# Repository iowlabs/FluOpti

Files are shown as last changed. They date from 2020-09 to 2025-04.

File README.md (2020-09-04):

# FluOpti
Este proyecto consiste en la realización de un control integrado para la iluminación del proyecto FluOpti. Más información respecto al poyecto se puede encontrar en los siguientes enlaces:
1. https://docs.google.com/document/d/1PmyignsIkzQdomBdSQQ2lFlBKneosc83GTr52-iTTBQ/edit?usp=sharing
2. [Git](https://github.com/SynBioUC/FluoPi/tree/master/Hardware_design_files/PCB)
3. [OSF](https://osf.io/dy6p2/)
4. [Manual de diseño de proyectos de LEDs estandar](https://www.overleaf.com/4759732231nspqcngnnhdq)

## Descripción de problema electrónico
El sistema consiste en un dispositivo que permite observar muestras biológicas, a las cuales se les realizan procesos de activación genética por medio de otpogenética. 
En la práctica, el dispositivo consiste en una cámara conectada a una raspberry, la que permite observar las muestras, un set de LEDs, los que permiten realizar los procesos optogenéticos, y la respectiva electrónica de control. 

Los LEDs que se deben controlar realizan 3 tareas distintas:
1. Excitar la muestra para poder adquirir imágenes de fluorescencia: LEDs azules.
2. Iluminar la muestra para obtener imágenes de campo claro que permitan medir el crecimiento de las colonias bacterianas de manera apropiada: LEDs blancos.
3. Generar estímulos para activación de procesos optogenéticos. Estos LEDs son de longitudes de onda específicas dependiendo del gen que se desee activar/desactivar: LEDs rojos y verdes.

El proyecto también considera la necesidad de implementar sensores que permitan calibrar el sistema y monitorear variables determinadas, tales como intensidad o temperatura.

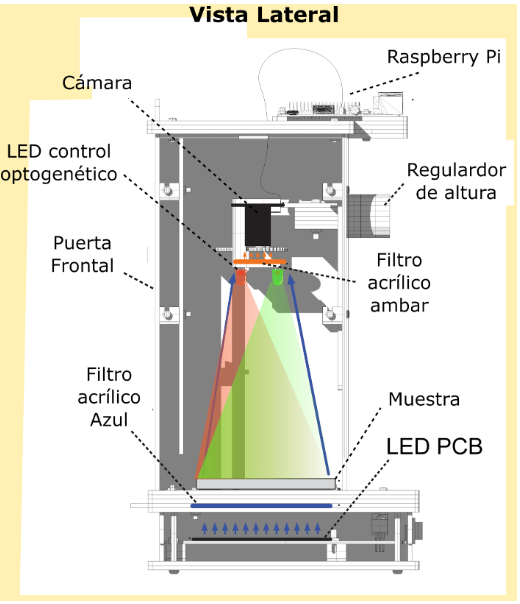
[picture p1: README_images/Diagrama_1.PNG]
Diagrama General


## Requerimientos

### Requerimientos generales
A continuación se enlista un set de requerimientos generales del proyecto:
1. Implementar una electrónica compatible con los componentes actuales disponibles.
2. Proponer una solución completa al problema.
3. Considerar diseños modulares que permitan adaptarse a parámetros futuros.

### Requerimientos específicos

A continuación se enlista un set de requerimientos específicos del proyecto:
1. Los LEDs azules empleados para iluminar la muestra corresponden a los [Super Bright 5mm Blue](https://www.superbrightleds.com/moreinfo/through-hole/5mm-blue-led-120-degree-viewing-angle-flat-tipped-1200-mcd/265/1192/):
   * Longitud de onda: 470nm
   * Forward current: 30mA @ 3.3V
   * Peak forward current: 100mA
   * Max voltage forward: 3.8V
   
2. Actualmente, se está pensando en una placa de LEDs azules con distribución física del tipo circular. Esto implicaría una cantidad de 55 LEDs. En la siguiente imagen se muestra esta topología propuesta:

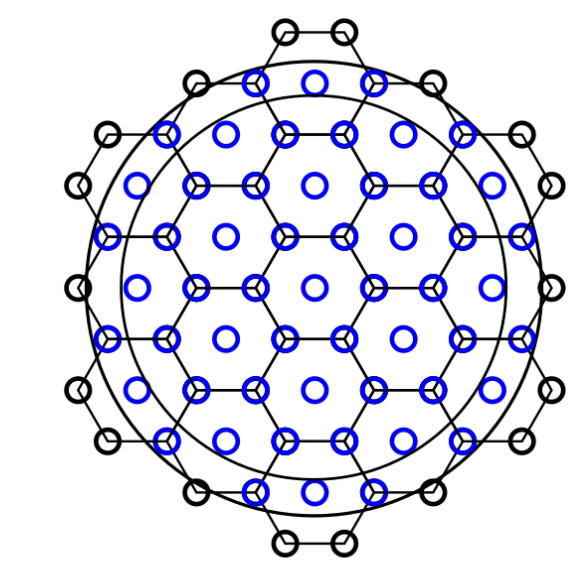
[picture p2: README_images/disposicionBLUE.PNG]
Propuesta nueva disposición LEDs azules


3. Los LEDs verdes empleados para la activación de genes corresponden a los [Kingbright WP7083ZGD/G](http://www.kingbrightusa.com/images/catalog/SPEC/WP7083ZGD-G.pdf):
   * Longitud de onda: 520nm
   * Forward current (typ): 20mA @ 3.2V
   * Peak forward current: 100mA
   * Max voltage forward: 4V
   
4. Los LEDs rojos empleados para la desactivación de genes corresponden a los [Deep-Red 5mm LED](https://www.ledsupply.com/leds/5mm-led-deep-red-660nm-50-degree-viewing-angle):
   * Longitud de onda: 660nm
   * Forward current (typ): 20mA @ 2.2V
   * Peak forward current: 100mA
   * Max voltage forward: 2.8V
   
5. Los LEDs blancos se implementan por medio de una tira LED comercial. Típicamente su operación se caracteriza por:
   * Forward current: 20mA @ 12V
   
6. El control implementado debe corresponder a PWM, con el fin de regular la intensidad lumínica de los LEDs. Se opta por este control debido a su sencilla implementación.

7. El sistema  debe contar con un sistema de distribución de potencia para alimentar todos los sub-módulos, LEDs y raspberry.

8. El sistema debe contar, además, con la posibilidad de leer sensores que permitan medir y calibrar la intensidad de luz proveniente desde los LEDs. Dado que el control se implementa por medio de una raspberry, es necesario utilizar sensores digitales o incluir en el diseño un ADC que permita realizar la conversión. En este último caso será necesaria la inclusión de una etapa que acondicione las señales provenientes desde los sensores.
   
9. El sensor de intensidad lumínica tiene que cumplir:
* Bajo costo
* Fácil de conseguir
* Respuesta plana para los LED Rojo y Verde

Una alternativa es el fototransistor [TEMT6000](https://learn.sparkfun.com/tutorials/temt6000-ambient-light-sensor-hookup-guide/all).

10. El sensor de temperatura es un NTC (termistor). [Aquí](https://www.adafruit.com/product/372) se presenta una alternativa.

11. El heater es del tipo resistivo y se debe poder alimentar con 9V ó 12V. Se debe implementar un control PWM de corriente utilizando un transistor. Una posible alternativa de heater es el [Film Heating Panel](http://www.icstation.com/heating-thin-film-polyimide-heating-plate-panel-25x50mm-b1221-p-9887.html).

### Consideraciones de diseño adicionales
   
1. Consideraciones de operación: El dispositivo debe ser diseñado para funcionar en espacios interiores y dentro de una cápsula cerrada, en la se realiza el análisis de las muestras, por lo que no es necesaria la resistencia al agua o a condiciones de humedad extremas. La placa estará, además, dentro de una caja, por lo que tampoco estará expuesta a polvo u otros contaminantes. Una vez instalado el dispositivo, este permanecerá siempre en el mismo lugar (a menos que se deba extraer por alguna situación en particular), por lo que no es necesario que el diseño considere la exposición a posibles golpes o vibraciones muy significativas.

2. La única etapa del circuito que puede significar un peligro para el usuario es la alimentación, puesto que esta proviene desde la red eléctrica, por lo cual es prudente que la carcasa del producto cumpla con normas acorde al voltaje y corriente de operación, por ejemplo, IP67. Sin embargo, esta protección será ajena al circuito mismo. Es pertinente, de todas formas, la inclusión de disipadores en algunos integrados, en el caso que operen con altas corrientes. Esto, para evitar fallas durante la operación o incluso que se quemen componentes.

## Propuesta
Teniendo presente los requerimientos planteados en la sección anterior se propone una solución basada en el siguiente esquema

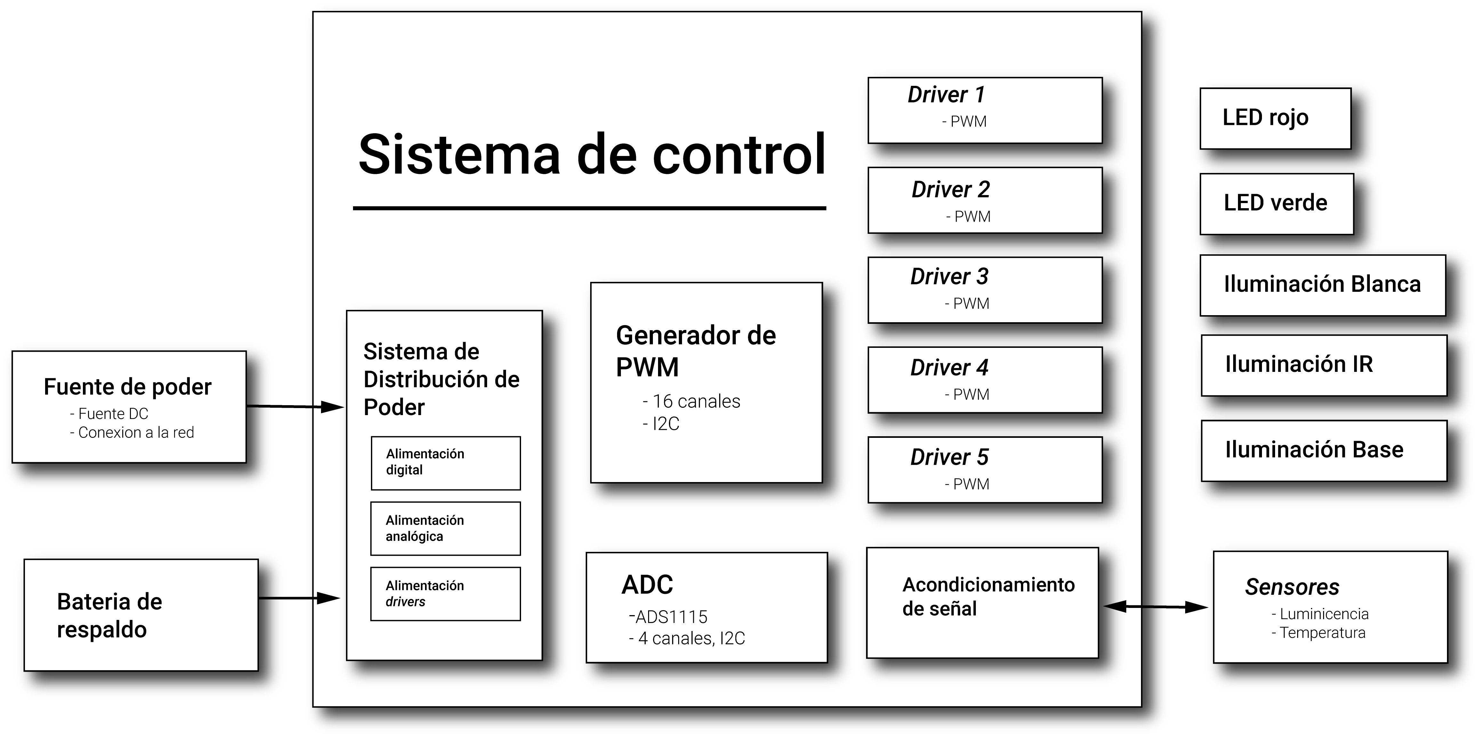
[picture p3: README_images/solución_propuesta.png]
Esquema de la solución electrónica propuesta


El principal criterio de diseño considerado es la modularidad, con el objetivo de poder entregar una solución adaptable y escalable. Los parámetros prácticos de elección de componentes dependen de los requerimientos específicos del sistema. El esquema general consiste en un módulo que genera señales PWM, el cual es controlado por protocolo serial I2C. Este módulo genera 16 señales de PWM permitiendo controlar hasta 16 canales. Estas señales PWM controlan los módulos driver. Estos últimos ajustan la señal PWM a los requerimientos que necesitan los distintos tipos de circuitos de LEDs. Cada driver puede poseer uno o más canales dependiendo de la cantidad de subcircuitos independientes que se deseen controlar por tipo de LED. Del mismo modo, algunas de estas señales de control PWM pueden dejarse a disposición del usuario en caso que necesite controlar una placa con driver ya existente, como es el caso de este proyecto. 

El otro bloque importante es el sistema de distribución de poder, el cual se encarga de generar todos los voltajes necesarios para los distintos bloques y etapas del circuito, dependiendo de cada requerimiento. La idea principal es que la placa reciba una única alimentación y que, internamente, genere los distintos voltajes y corrientes, contribuyendo, así, a la adaptabilidad de la solución.

Por último, la placa considera la inclusión de un ADC de 4 canales, controlado por I2C, el cual permite leer hasta 4 sensores analógicos. Es necesario contar con un ADC, ya que la Raspberry Pi no cuenta con ADC. Esto permite otorgar una alta adaptabilidad, ya que es posible conectar distintos tipos de sensores analógicos, dependiendo de la aplicación. Para esto, la placa considera etapas de acondicionamiento de señal, las cuales se deben configurar para el sensor específico.

### Resumen de características de la solución propuesta

Las principales características de la solución propuesta son:

1. Adaptabilidad: La placa total solo se controla por medio de un bus I2C (3 pines), independiente de la cantidad de LEDs y sensores que se deseen utilizar. 

2. Integración: La disposición de canales de control PWM permite integrar tanto las soluciones existentes como soluciones creadas por distintos fabricantes.

3. Escalabilidad: Gracias a la utilización del protocolo I2C, es posible controlar múltiples de estas placas con una sola Raspberry Pi (o un solo microcontrolador/procesador en general). Si se integran dos placas en serie se puede llegar a disponer de 32 canales de control de LEDs y 8 canales de sensores analógicos. 

A continuación, se describen en detalle los módulos a implementar. Es importante mencionar que se utilizó como guía el [documento tutorial](https://www.overleaf.com/4759732231nspqcngnnhdq) generado en el marco de este proyecto.

### Detalle de módulos

#### ADC
El ADC escogido es el [ADC](https://cdn-shop.adafruit.com/datasheets/ads1115.pdf) de la empresa Texas Instruments. La empresa [adafruit](https://www.adafruit.com/product/1085) posee un módulo autocontenido para integrar este ADC a la Raspberry Pi, así como una completa documentación y las bibliotecas para utilizarlo. 

Las principales características de este ADC se enlistan a continuación

* 4 canales, single-ended.
* 16 bits de resolución
* Voltaje de alimentación entre 2V a 5V
* Interfaz I2C
* Referencia interna

#### Acondicionamiento de señal
Los sensores que se utilizarán permiten implementar el proceso de medición gracias a la variación de sus propiedades eléctricas. En general, estas variaciones se evidencian mediante un cambio de voltaje. En consecuencia, este es el voltaje que debe ser adquirido por el circuito electrónico. Por ello, en primera instancia, se dispone de un circuito divisor que, al ser conectado con el respectivo sensor, permite obtener el voltaje asociado a la medición. En la siguiente figura se muestra un ejemplo de esta conexión circuital, para el caso de un sensor de temperatura del tipo termistor (NTC):

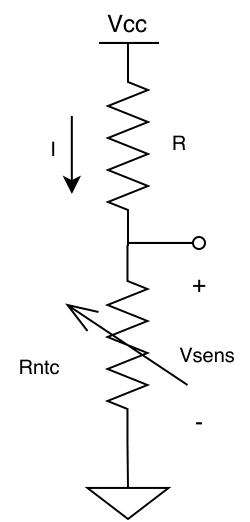
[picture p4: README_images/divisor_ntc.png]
Divisor


Para realizar correctamente la adquisición de las señales desde los sensores es necesario contar con una etapa de acondicionamiento de señal. De esta forma, se asegura que los valores de voltaje que entreguen los sensores se encuentren dentro de los límites que permiten las entradas del ADC y de la Raspberry. No solo es deseable que se opere dentro de los límites, sino también aprovechar el rango de lectura al máximo, es decir, que el voltaje mínimo de medición sea igual (o lo más cercano posible) al voltaje mínimo que permiten los pines del ADC. Y, la misma relación con el voltaje máximo de medición. 

Dado que aún no existe 100% de certeza sobre los sensores a utilizar, se implementó una circuito genérico de acondicionamiento, el cual se compone de una etapa de amplificación y otra de adición de offset. En la siguiente figura se muestra este circuito:

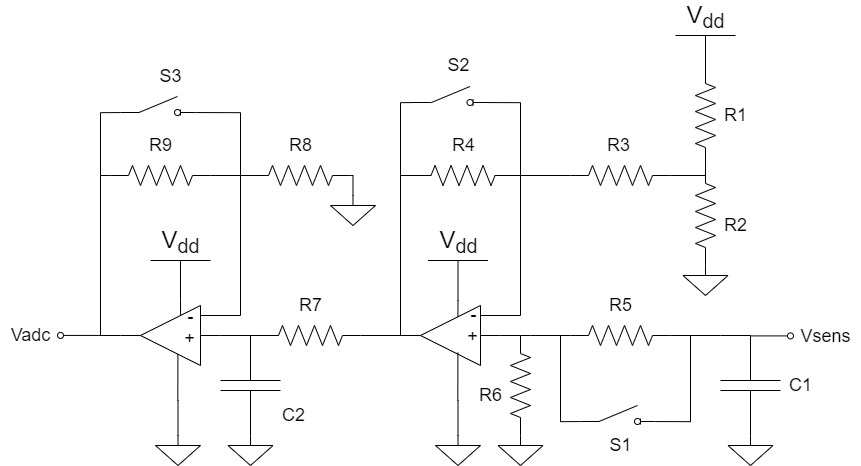
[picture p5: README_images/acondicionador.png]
Acondicionador


Los símbolos de switches corresponden, en la práctica, a un solder jumper, el cual conecta la entrada con la salida solo si se unen con soldadura sus terminales. Si se conectan S1, S2 y S3 el circuito queda configurado como un buffer, lo cual, de todas formas, beneficia a la señal adquirida puesto que el buffer disminuye su impedancia. Conectando o no S1, S2 y S3 se pueden obtener distintas configuraciones: solo amplificador, solo adición de offset, o ambas. Además, los valores de las resistencias se pueden ajustar dependiendo de los sensores que se utilicen, de tal forma de fijar correctamente la ganancia y el offset, según sea el caso.

#### Generador de PWM
La generación de PWM se realiza por medio de un circuito integrado [PCA9685](https://cdn-shop.adafruit.com/datasheets/PCA9685.pdf). La empresa [adafruit](https://www.adafruit.com/product/2928) posee un módulo autocontenido para integrar este módulo a la Raspberry Pi, así como una documentación completa y las bibliotecas para utilizarlo. 

Principales características:

* 16 canales dimeables por PWM.
* 12 bits de resolución
* Voltaje de alimentación etre 2.3V a 5.5V
* Interfaz I2C

#### Driver de baja corriente

Para los canales de bajo consumo de corriente, tales como los arreglos de LEDs rojos y verdes, se utilizará el integrado [ULN2803](https://www.electroschematics.com/wp-content/uploads/2013/07/uln2803a-datasheet.pdf). Este integrado implementa un arreglo de 8 transistores tipo darlington, haciendo posible el control de hasta 8 canales en un único integrado.

Principales características:

* Arreglo de 8 canales
* Poseen alimentación común
* La corriente máxima por canal es de 500mA, pudiendo aumentar esta cantidad si se consideran canales en paralelo.

#### Driver de alta corriente
Para los canales de alto consumo se utilizará un transistor mosfet [IRF740](https://datasheet.lcsc.com/szlcsc/1808281645_Infineon-Technologies-IRF7402TRPBF_C169089.pdf). Es necesario contar con un transistor por canal. Y, para casos de alta corriente (superiores a 1A) es necesario considerar la inclusión de disipadores (heatsink) o pads de disipación que permitan una evacuación efectiva del calor.

Principales características:

* Altas frecuencias de switching
* Bajo consumo de operación 
* Control de hasta 10A (ó 40A en corrientes pulsantes)
* Simple implementación

#### Sistema de distribución de poder

Como se mencionará más adelante, la alimentación que llegará al circuito electrónico implementado será de 12VDC, por lo que es necesario contar con convertidores de voltaje DC-DC para generar los distintos voltajes de alimentación que se requieren en el circuito. En particular, es necesario generar 5V y 3.3V para alimentar los circuitos analógicos y digitales, y un set de voltajes para alimentar los distintos arreglos de LEDs y el Heater. Se decidió disponer de los siguientes voltajes para este último uso: 9V, 16V, 20V y 24V. A continuación se especifican los convertidores empleados para generar cada uno de los voltajes mencionados.

##### 5V
* Integrado: [LM2596R-5.0](https://datasheet.lcsc.com/szlcsc/1811131510_HTC-Korea-TAEJIN-Tech-LM2596R-5-0_C77782.pdf)
* Tipo: Step-down, regulador switching
* Frecuencia de switcheo: 150kHz
* Corriente máxima de salida: 3A

##### 3.3V
* Integrado: [AP2112K-3.3](https://datasheet.lcsc.com/szlcsc/1809192242_Diodes-Incorporated-AP2112K-3-3TRG1_C51118.pdf)
* Tipo: LDO, regulador lineal
* Corriente máxima de salida: 600mA

##### 9V
* Integrado: [LM2696SX-ADJ](https://datasheet.lcsc.com/szlcsc/1809192335_Texas-Instruments-LM2596SX-ADJ-NOPB_C29781.pdf)
* Tipo: Step-down, regulador switching ajustable (voltaje de salida es configurable según indicaciones de conexión en el datasheet)
* Frecuencia de switcheo: 150kHz
* Corriente máxima de salida: 3A

##### 16V, 20V, 24V
* Integrado: [XL6008E1](https://datasheet.lcsc.com/szlcsc/1809200019_XLSEMI-XL6008E1_C73012.pdf)
* Tipo: Step-up, regulador switching ajustable (voltaje de salida es configurable según indicaciones de conexión en el datasheet)
* Frecuencia de switcheo: 400kHz
* Corriente máxima de salida: 3A

#### Fuente de alimentación

Dado que el circuito electrónico funcionará con alimentación DC es necesario emplear una fuente DC que se enchufe directamente a la red y que entegue un voltaje de salida continuo. En particular, se decidió emplear una [fuente DC conmutada](https://afel.cl/producto/fuente-de-poder-12v-10a-120w/). Sus principales características son:

* Voltaje de entrada: 100-120VAC / 60Hz, **200-240VAC / 50Hz**
* Voltaje de salida: 12V
* Corriente máxima de salida: 10A
* Potencia máxima de salida: 120W

## Esquemático

En la siguiente figura se muestra el diagrama de bloques del esquemático implementado

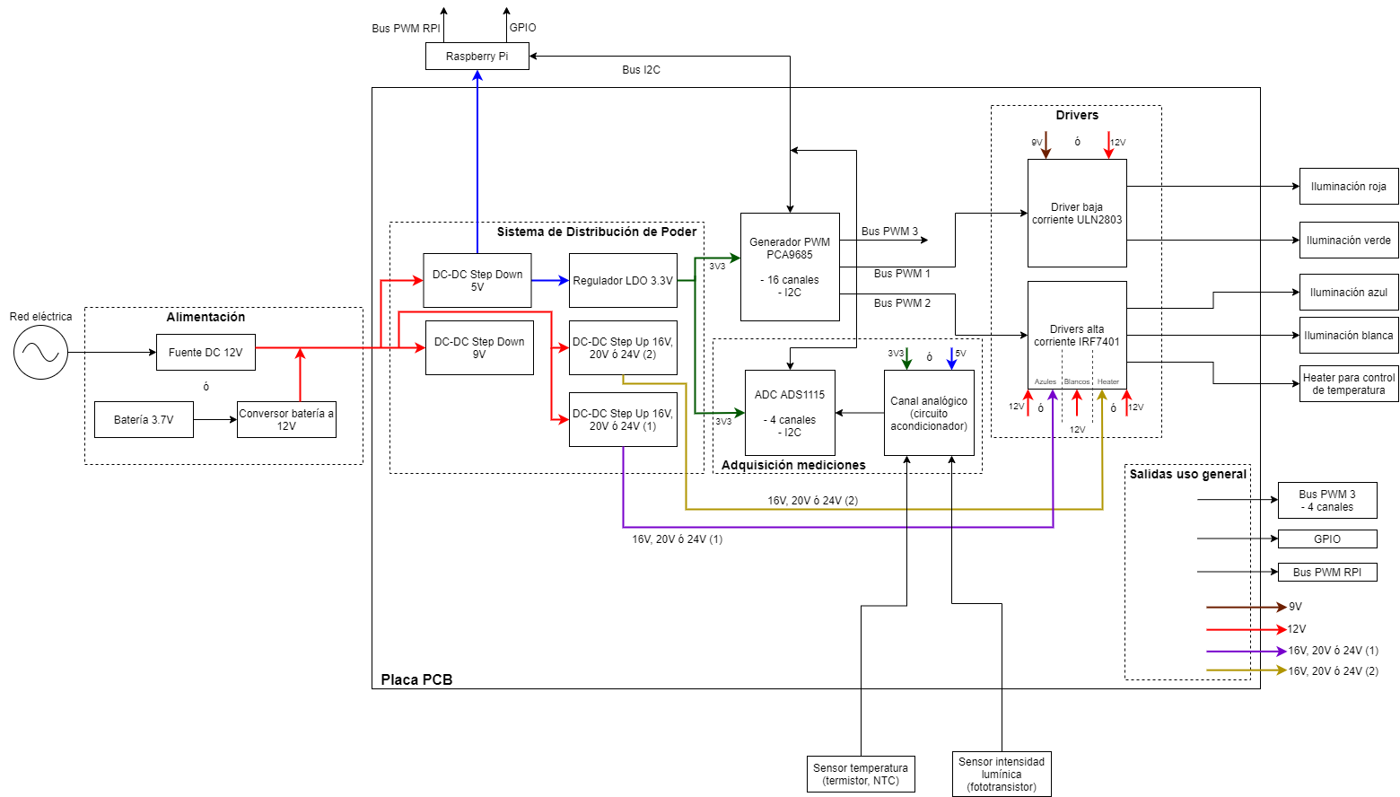
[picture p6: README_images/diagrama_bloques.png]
Diagrama de bloques del esquemático


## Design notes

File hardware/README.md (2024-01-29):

# FluOpti Electrónica

FluOpti es una dispositivo controlador de LEDs para aplicaciones optogenéticas dentro del contexto del proyecto FluOpti.

La placa desarrollada contiene la electrónica necesaria para controlar fuentes de iluminación de alto consumo basadas en LEDS. Dependiendo de la cantidad de LEDs utilizadas y el tipo de conexión en que se dispongan estas matrices de LEDs pueden variar tanto en consumo como el el voltaje de operación.

Es por esto que la electrónica diseñada fue desarrollada considerando flexibilidad en su implementación para abordar un gran  numero de escenarios.

Cuenta con 4 canales de alta potencia para aborar cargas de 24 20 16 12 V configurables y potencias de ahasta

### Features

 La placa cuenta principalmente con 4 canales para controlar canales de LEDS

 - Canal de alta potencia para LEDs azules
 - 3 canales de baja potencia para LEDs Rojos, Verdes, Blancas.

Adicionalmente la placa implementa un controlador de temperatura, para esto cuenta con la electrónica necesaria para drivear 2 heaters resistivos, y con la capacidad de conectar hasta 4 sensores de temperatura NTC analógicos.

## Descripción de Hardware

El esquema presentado en la siguiente figura presenta una descripción general de la estructura del hardware desarrollado.  

Esquema de la solución electrónica propuesta

El principal criterio de diseño considerado es la modularidad, con el objetivo de poder entregar una solución adaptable y escalable. El esquema general consiste en un módulo que genera señales PWM, el cual es controlado por protocolo serial I2C. Este módulo genera 16 señales de PWM permitiendo controlar hasta 16 canales. Estas señales PWM controlan los módulos driver que se encargan de adaptarse a los requerimientos de corriente y voltaje de las cargas asociadas. Cada driver puede poseer uno o más canales dependiendo de la cantidad de subcircuitos independientes que se deseen controlar por tipo de LED. Del mismo modo, algunas de estas señales de control PWM fueron dejadas a disposición del usuario en caso que necesite controlar una placa con driver ya existente, como es el caso de este proyecto (compatibilidad con diseños anteriores).

El otro bloque importante es el sistema de distribución de poder, el cual se encarga de generar todos los voltajes necesarios para los distintos bloques y etapas del circuito, dependiendo de cada requerimiento. La idea principal es que la placa reciba una única alimentación y que, internamente, genere los distintos voltajes y corrientes, contribuyendo, así, a la adaptabilidad de la solución.

Por último, la placa considera la inclusión de un ADC de 4 canales, controlado por I2C, el cual permite leer hasta 4 sensores analógicos para implementar los sensores de corriente. Es necesario contar con un ADC, ya que la Raspberry Pi no cuenta con ADC. Esto permite otorgar una alta adaptabilidad, ya que es posible conectar distintos tipos de sensores analógicos, dependiendo de la aplicación. Para esto, la placa considera etapas de acondicionamiento de señal, las cuales se deben configurar para el sensor específico.

### Resumen de características de la solución propuesta

Las principales características de la solución propuesta son:

1. Adaptabilidad: La placa total solo se controla por medio de un bus I2C (3 pines), independiente de la cantidad de LEDs y sensores que se deseen utilizar.

2. Integración: La disposición de canales de control PWM permite integrar tanto las soluciones existentes como soluciones creadas por distintos fabricantes.

3. Escalabilidad: Gracias a la utilización del protocolo I2C, es posible controlar múltiples de estas placas con una sola Raspberry Pi (o un solo microcontrolador/procesador en general). Si se integran dos placas en serie se puede llegar a disponer de 32 canales de control de LEDs y 8 canales de sensores analógicos.

A continuación, se describen en detalle los módulos a implementar. Es importante mencionar que se utilizó como guía el [documento tutorial](https://www.overleaf.com/4759732231nspqcngnnhdq) generado en el marco de este proyecto.

### Detalle de módulos

#### ADC
El ADC escogido es el [ADC](https://cdn-shop.adafruit.com/datasheets/ads1115.pdf) de la empresa Texas Instruments. La empresa [adafruit](https://www.adafruit.com/product/1085) posee un módulo autocontenido para integrar este ADC a la Raspberry Pi, así como una completa documentación y las bibliotecas para utilizarlo.

Las principales características de este ADC se enlistan a continuación

* 4 canales, single-ended.
* 16 bits de resolución
* Voltaje de alimentación entre 2V a 5V
* Interfaz I2C
* Referencia interna

#### Acondicionamiento de señal
Los sensores que se utilizarán permiten implementar el proceso de medición gracias a la variación de sus propiedades eléctricas. En general, estas variaciones se evidencian mediante un cambio de voltaje. En consecuencia, este es el voltaje que debe ser adquirido por el circuito electrónico. Por ello, en primera instancia, se dispone de un circuito divisor que, al ser conectado con el respectivo sensor, permite obtener el voltaje asociado a la medición. En la siguiente figura se muestra un ejemplo de esta conexión circuital, para el caso de un sensor de temperatura del tipo termistor (NTC):

Divisor

Para realizar correctamente la adquisición de las señales desde los sensores es necesario contar con una etapa de acondicionamiento de señal. De esta forma, se asegura que los valores de voltaje que entreguen los sensores se encuentren dentro de los límites que permiten las entradas del ADC y de la Raspberry. No solo es deseable que se opere dentro de los límites, sino también aprovechar el rango de lectura al máximo, es decir, que el voltaje mínimo de medición sea igual (o lo más cercano posible) al voltaje mínimo que permiten los pines del ADC. Y, la misma relación con el voltaje máximo de medición.

Dado que aún no existe 100% de certeza sobre los sensores a utilizar, se implementó una circuito genérico de acondicionamiento, el cual se compone de una etapa de amplificación y otra de adición de offset. En la siguiente figura se muestra este circuito:

Acondicionador

Los símbolos de switches corresponden, en la práctica, a un solder jumper, el cual conecta la entrada con la salida solo si se unen con soldadura sus terminales. Si se conectan S1, S2 y S3 el circuito queda configurado como un buffer, lo cual, de todas formas, beneficia a la señal adquirida puesto que el buffer disminuye su impedancia. Conectando o no S1, S2 y S3 se pueden obtener distintas configuraciones: solo amplificador, solo adición de offset, o ambas. Además, los valores de las resistencias se pueden ajustar dependiendo de los sensores que se utilicen, de tal forma de fijar correctamente la ganancia y el offset, según sea el caso.

#### Generador de PWM
La generación de PWM se realiza por medio de un circuito integrado [PCA9685](https://cdn-shop.adafruit.com/datasheets/PCA9685.pdf). La empresa [adafruit](https://www.adafruit.com/product/2928) posee un módulo autocontenido para integrar este módulo a la Raspberry Pi, así como una documentación completa y las bibliotecas para utilizarlo.

Principales características:

* 16 canales dimeables por PWM.
* 12 bits de resolución
* Voltaje de alimentación etre 2.3V a 5.5V
* Interfaz I2C

#### Driver de baja corriente

Para los canales de bajo consumo de corriente, tales como los arreglos de LEDs rojos y verdes, se utilizará el integrado [ULN2803](https://www.electroschematics.com/wp-content/uploads/2013/07/uln2803a-datasheet.pdf). Este integrado implementa un arreglo de 8 transistores tipo darlington, haciendo posible el control de hasta 8 canales en un único integrado.

Principales características:

* Arreglo de 8 canales
* Poseen alimentación común
* La corriente máxima por canal es de 500mA, pudiendo aumentar esta cantidad si se consideran canales en paralelo.

#### Driver de alta corriente
Para los canales de alto consumo se utilizará un transistor mosfet [IRF740](https://datasheet.lcsc.com/szlcsc/1808281645_Infineon-Technologies-IRF7402TRPBF_C169089.pdf). Es necesario contar con un transistor por canal. Y, para casos de alta corriente (superiores a 1A) es necesario considerar la inclusión de disipadores (heatsink) o pads de disipación que permitan una evacuación efectiva del calor.

Principales características:

* Altas frecuencias de switching
* Bajo consumo de operación
* Control de hasta 10A (ó 40A en corrientes pulsantes)
* Simple implementación

#### Sistema de distribución de poder

Como se mencionará más adelante, la alimentación que llegará al circuito electrónico implementado será de 12VDC, por lo que es necesario contar con convertidores de voltaje DC-DC para generar los distintos voltajes de alimentación que se requieren en el circuito. En particular, es necesario generar 5V y 3.3V para alimentar los circuitos analógicos y digitales, y un set de voltajes para alimentar los distintos arreglos de LEDs y el Heater. Se decidió disponer de los siguientes voltajes para este último uso: 9V, 16V, 20V y 24V. A continuación se especifican los convertidores empleados para generar cada uno de los voltajes mencionados.

##### 5V
* Integrado: [LM2596R-5.0](https://datasheet.lcsc.com/szlcsc/1811131510_HTC-Korea-TAEJIN-Tech-LM2596R-5-0_C77782.pdf)
* Tipo: Step-down, regulador switching
* Frecuencia de switcheo: 150kHz
* Corriente máxima de salida: 3A

##### 3.3V
* Integrado: [AP2112K-3.3](https://datasheet.lcsc.com/szlcsc/1809192242_Diodes-Incorporated-AP2112K-3-3TRG1_C51118.pdf)
* Tipo: LDO, regulador lineal
* Corriente máxima de salida: 600mA

##### 9V
* Integrado: [LM2696SX-ADJ](https://datasheet.lcsc.com/szlcsc/1809192335_Texas-Instruments-LM2596SX-ADJ-NOPB_C29781.pdf)
* Tipo: Step-down, regulador switching ajustable (voltaje de salida es configurable según indicaciones de conexión en el datasheet)
* Frecuencia de switcheo: 150kHz
* Corriente máxima de salida: 3A

##### 16V, 20V, 24V
* Integrado: [XL6008E1](https://datasheet.lcsc.com/szlcsc/1809200019_XLSEMI-XL6008E1_C73012.pdf)
* Tipo: Step-up, regulador switching ajustable (voltaje de salida es configurable según indicaciones de conexión en el datasheet)
* Frecuencia de switcheo: 400kHz
* Corriente máxima de salida: 3A

#### Fuente de alimentación

Dado que el circuito electrónico funcionará con alimentación DC es necesario emplear una fuente DC que se enchufe directamente a la red y que entegue un voltaje de salida continuo. En particular, se decidió emplear una [fuente DC conmutada](https://afel.cl/producto/fuente-de-poder-12v-10a-120w/). Sus principales características son:

* Voltaje de entrada: 100-120VAC / 60Hz, **200-240VAC / 50Hz**
* Voltaje de salida: 12V
* Corriente máxima de salida: 10A
* Potencia máxima de salida: 120W

## Esquemático

En la siguiente figura se muestra el diagrama de bloques del esquemático implementado

Diagrama de bloques del esquemático

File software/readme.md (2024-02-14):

# Hardware

En la Raspberry Pi:
  - pin 3 (GPIO2): SDA
  - pin 5 (GPIO3): SCL
  - pin 6 :        GND

En la tarjeta FLuOpti
  Esquina superior izquierda:<br>
    1 - SCL &emsp; &emsp; &emsp; &emsp; &emsp;8 - PWM in 1<br>
    2 - SDA &emsp; &emsp; &emsp; &emsp; &ensp;&nbsp;7 - PWM in 2<br>
    3 - NotConnected   &emsp; 6 - GPIO1<br>
    4 - GND &emsp; &emsp; &emsp; &emsp; &ensp;5 - GPIO2<br>
  
  Los conectores GPIO y PWM estan diseñados para conectar cualquier pin de la Raspberry Pi, los cuales son clonados a la parte inferior de la placa. *e.g.* puedo conectar el pin15 de la raspberry Pi al conector GPIO1, y luego conectarme directamente al GPIO1 de la parte inferior de la placa para acceder a él.

 De manera alternativa, es preferible usar el conector i2c (esquina superior derecha) para mayor simpleza:<br>
  1 - SCL<br>
  2 - SDA<br>
  3 - GND

<p align="center">
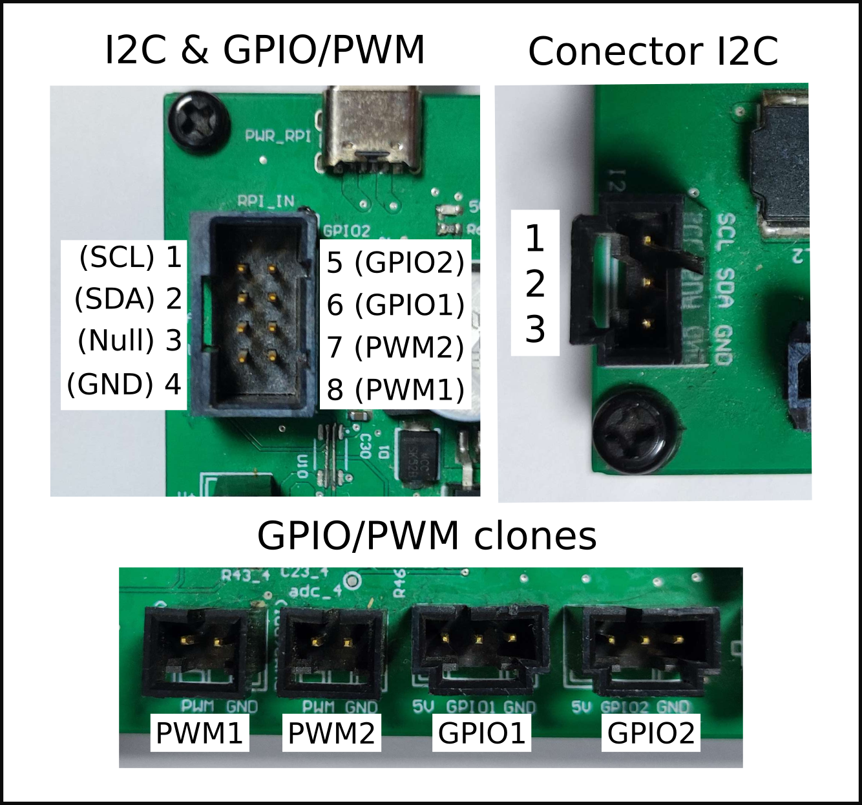
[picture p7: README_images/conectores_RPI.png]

</p>
  
# Instalación

## Sistemas operativos previos a BookWorm

Instalar las librerias necesarias para el funcionamiento de la placa:
```
sudo pip install adafruit-ADS1x15
sudo pip install adafruit-pca9685
sudo pip install simple-pid
```

## Sistema operativo BookWorm
Si se esta usando *BookWorm* como sistema operativo de la Raspberry Pi, es necesario crear un ambiente en el que instalar estas librerias.
Primero asegurarse de tener todo actualizado:
```
sudo apt-get update
sudo apt-get upgrade
sudo apt-get install python3-pip
sudo apt install --upgrade python3-setuptools
sudo apt install python3.11-venv
```

Crear el ambiente *fluop_env*:
```
python3 -m venv fluop_env --system-site-packages
```
y activarlo
```
source fluop_env/bin/activate
```

ahora se deben instalar las librerias en él:
```
pip3 install adafruit-ADS1x15
pip3 install adafruit-pca9685
pip3 install simple-pid
```

Alternativamente se pueden instalar las librerias directamente en el sistema (sin crear ambientes), agregando el comando *--break-system-packages*. Ejemplo:
```
sudo pip install adafruit-ADS1x15 --break-system-packages
```

## Activar comunicación I2C

Ejecutar *sudo raspi-config*, ir a *opciones de interface* y activar la comunicación I2C.

# Solución de problemas

1. Se recomienda instalar el scan de i2c para revisar si los módulos estan:
  - https://learn.adafruit.com/scanning-i2c-addresses/raspberry-pi
  - sudo apt-get install i2c-tools
  - run: i2cdetect -y 1

Se desplegará la lista de direcciones de los módulos conectados:
```
     0  1  2  3  4  5  6  7  8  9  a  b  c  d  e  f
00:                         -- -- -- -- -- -- -- --
10: -- -- -- -- -- -- -- -- -- -- -- -- -- -- -- --
20: -- -- -- -- -- -- -- -- -- -- -- -- -- -- -- --
30: -- -- -- -- -- -- -- -- -- -- -- -- -- -- -- -- 
40: -- -- -- -- -- -- -- -- -- 49 -- -- -- -- -- -- 
50: -- -- -- -- -- -- -- -- -- -- -- -- 5c -- -- -- 
60: -- -- -- -- -- -- -- -- -- -- -- -- -- -- -- -- 
70: 70 -- -- -- -- -- -- --  
```
vemos que hay módulos conectados en 0x49, 0x5c y 0x77

En caso de que los módulos no se encuentren conectados, se desplegará la lista vacia:
```
     0  1  2  3  4  5  6  7  8  9  a  b  c  d  e  f
00:                         -- -- -- -- -- -- -- -- 
10: -- -- -- -- -- -- -- -- -- -- -- -- -- -- -- -- 
20: -- -- -- -- -- -- -- -- -- -- -- -- -- -- -- -- 
30: -- -- -- -- -- -- -- -- -- -- -- -- -- -- -- -- 
40: -- -- -- -- -- -- -- -- -- -- -- -- -- -- -- -- 
50: -- -- -- -- -- -- -- -- -- -- -- -- -- -- -- -- 
60: -- -- -- -- -- -- -- -- -- -- -- -- -- -- -- -- 
70: -- -- -- -- -- -- -- --  
```

# Testeo

En la terminal, navegar hasta el directorio del software */FluOpti/software* (usando comando cd).
(debe estar clonado el repositorio FluOpti en la raspberry).

si se esta utilizando BookWorm como sistema operativo de la raspberry, se debe activar el ambiente en el cual se instalaron los paquetes. Si el ambiente creado se llama *fluop_env*:

```
source fluop_env/bin/activate
```

Luego ejecutamos la rutina de testeo mediante el comando:
```
python3 simple_test.py
```
es necesario chequear que los LEDs esten conectados de manera correspondiente a las posiciones indicadas en el código *FluOpti.py*
```
 self._default_modules  = {
        #MODULE  #CHANNEL    #VALUE
        'R'    :{ 'chan':5, 'value': 0,'status':0},
        'G'    :{ 'chan':6, 'value': 0,'status':0},
        'B'    :{ 'chan':9, 'value': 0,'status':0},
        'W'    :{ 'chan':10, 'value': 0,'status':0},
        'H1'   :{ 'chan':11, 'value': 0,'status':0},
        'H2'   :{ 'chan':12, 'value': 0,'status':0}
        }
```

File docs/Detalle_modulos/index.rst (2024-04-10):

Detalle de módulos
~~~~~~~~~~~~~~~~~~

ADC
^^^

El ADC escogido es el
`ADC <https://cdn-shop.adafruit.com/datasheets/ads1115.pdf>`__ de la
empresa Texas Instruments. La empresa
`adafruit <https://www.adafruit.com/product/1085>`__ posee un módulo
autocontenido para integrar este ADC a la Raspberry Pi, así como una
completa documentación y las bibliotecas para utilizarlo.

Las principales características de este ADC se enlistan a continuación

-  4 canales, single-ended.
-  16 bits de resolución
-  Voltaje de alimentación entre 2V a 5V
-  Interfaz I2C
-  Referencia interna

Acondicionamiento de señal
^^^^^^^^^^^^^^^^^^^^^^^^^^

Los sensores que se utilizarán permiten implementar el proceso de
medición gracias a la variación de sus propiedades eléctricas. En
general, estas variaciones se evidencian mediante un cambio de voltaje.
En consecuencia, este es el voltaje que debe ser adquirido por el
circuito electrónico. Por ello, en primera instancia, se dispone de un
circuito divisor que, al ser conectado con el respectivo sensor, permite
obtener el voltaje asociado a la medición. En la siguiente figura se
muestra un ejemplo de esta conexión circuital, para el caso de un sensor
de temperatura del tipo termistor (NTC):

Divisor

   Divisor

Para realizar correctamente la adquisición de las señales desde los
sensores es necesario contar con una etapa de acondicionamiento de
señal. De esta forma, se asegura que los valores de voltaje que
entreguen los sensores se encuentren dentro de los límites que permiten
las entradas del ADC y de la Raspberry. No solo es deseable que se opere
dentro de los límites, sino también aprovechar el rango de lectura al
máximo, es decir, que el voltaje mínimo de medición sea igual (o lo más
cercano posible) al voltaje mínimo que permiten los pines del ADC. Y, la
misma relación con el voltaje máximo de medición.

Dado que aún no existe 100% de certeza sobre los sensores a utilizar, se
implementó una circuito genérico de acondicionamiento, el cual se
compone de una etapa de amplificación y otra de adición de offset. En la
siguiente figura se muestra este circuito:

Acondicionador

   Acondicionador

Los símbolos de switches corresponden, en la práctica, a un solder
jumper, el cual conecta la entrada con la salida solo si se unen con
soldadura sus terminales. Si se conectan S1, S2 y S3 el circuito queda
configurado como un buffer, lo cual, de todas formas, beneficia a la
señal adquirida puesto que el buffer disminuye su impedancia. Conectando
o no S1, S2 y S3 se pueden obtener distintas configuraciones: solo
amplificador, solo adición de offset, o ambas. Además, los valores de
las resistencias se pueden ajustar dependiendo de los sensores que se
utilicen, de tal forma de fijar correctamente la ganancia y el offset,
según sea el caso.

Generador de PWM
^^^^^^^^^^^^^^^^

La generación de PWM se realiza por medio de un circuito integrado
`PCA9685 <https://cdn-shop.adafruit.com/datasheets/PCA9685.pdf>`__. La
empresa `adafruit <https://www.adafruit.com/product/2928>`__ posee un
módulo autocontenido para integrar este módulo a la Raspberry Pi, así
como una documentación completa y las bibliotecas para utilizarlo.

Principales características:

-  16 canales dimeables por PWM.
-  12 bits de resolución
-  Voltaje de alimentación etre 2.3V a 5.5V
-  Interfaz I2C

Driver de baja corriente
^^^^^^^^^^^^^^^^^^^^^^^^

Para los canales de bajo consumo de corriente, tales como los arreglos
de LEDs rojos y verdes, se utilizará el integrado
`ULN2803 <https://www.electroschematics.com/wp-content/uploads/2013/07/uln2803a-datasheet.pdf>`__.
Este integrado implementa un arreglo de 8 transistores tipo darlington,
haciendo posible el control de hasta 8 canales en un único integrado.

Principales características:

-  Arreglo de 8 canales
-  Poseen alimentación común
-  La corriente máxima por canal es de 500mA, pudiendo aumentar esta
   cantidad si se consideran canales en paralelo.

Driver de alta corriente
^^^^^^^^^^^^^^^^^^^^^^^^

Para los canales de alto consumo se utilizará un transistor mosfet
`IRF740 <https://datasheet.lcsc.com/szlcsc/1808281645_Infineon-Technologies-IRF7402TRPBF_C169089.pdf>`__.
Es necesario contar con un transistor por canal. Y, para casos de alta
corriente (superiores a 1A) es necesario considerar la inclusión de
disipadores (heatsink) o pads de disipación que permitan una evacuación
efectiva del calor.

Principales características:

-  Altas frecuencias de switching
-  Bajo consumo de operación
-  Control de hasta 10A (ó 40A en corrientes pulsantes)
-  Simple implementación

Sistema de distribución de poder
^^^^^^^^^^^^^^^^^^^^^^^^^^^^^^^^

Como se mencionará más adelante, la alimentación que llegará al circuito
electrónico implementado será de 12VDC, por lo que es necesario contar
con convertidores de voltaje DC-DC para generar los distintos voltajes
de alimentación que se requieren en el circuito. En particular, es
necesario generar 5V y 3.3V para alimentar los circuitos analógicos y
digitales, y un set de voltajes para alimentar los distintos arreglos de
LEDs y el Heater. Se decidió disponer de los siguientes voltajes para
este último uso: 9V, 16V, 20V y 24V. A continuación se especifican los
convertidores empleados para generar cada uno de los voltajes
mencionados.

5V
''

-  Integrado:
   `LM2596R-5.0 <https://datasheet.lcsc.com/szlcsc/1811131510_HTC-Korea-TAEJIN-Tech-LM2596R-5-0_C77782.pdf>`__
-  Tipo: Step-down, regulador switching
-  Frecuencia de switcheo: 150kHz
-  Corriente máxima de salida: 3A

.. _v-1:

3.3V
''''

-  Integrado:
   `AP2112K-3.3 <https://datasheet.lcsc.com/szlcsc/1809192242_Diodes-Incorporated-AP2112K-3-3TRG1_C51118.pdf>`__
-  Tipo: LDO, regulador lineal
-  Corriente máxima de salida: 600mA

.. _v-2:

9V
''

-  Integrado:
   `LM2696SX-ADJ <https://datasheet.lcsc.com/szlcsc/1809192335_Texas-Instruments-LM2596SX-ADJ-NOPB_C29781.pdf>`__
-  Tipo: Step-down, regulador switching ajustable (voltaje de salida es
   configurable según indicaciones de conexión en el datasheet)
-  Frecuencia de switcheo: 150kHz
-  Corriente máxima de salida: 3A

16V, 20V, 24V
'''''''''''''

-  Integrado:
   `XL6008E1 <https://datasheet.lcsc.com/szlcsc/1809200019_XLSEMI-XL6008E1_C73012.pdf>`__
-  Tipo: Step-up, regulador switching ajustable (voltaje de salida es
   configurable según indicaciones de conexión en el datasheet)
-  Frecuencia de switcheo: 400kHz
-  Corriente máxima de salida: 3A

Fuente de alimentación
^^^^^^^^^^^^^^^^^^^^^^

Dado que el circuito electrónico funcionará con alimentación DC es
necesario emplear una fuente DC que se enchufe directamente a la red y
que entegue un voltaje de salida continuo. En particular, se decidió
emplear una `fuente DC
conmutada <https://afel.cl/producto/fuente-de-poder-12v-10a-120w/>`__.
Sus principales características son:

-  Voltaje de entrada: 100-120VAC / 60Hz, **200-240VAC / 50Hz**
-  Voltaje de salida: 12V
-  Corriente máxima de salida: 10A
-  Potencia máxima de salida: 120W

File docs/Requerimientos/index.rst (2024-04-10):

Requerimientos
--------------

Requerimientos generales
~~~~~~~~~~~~~~~~~~~~~~~~

A continuación se enlista un set de requerimientos generales del
proyecto: 1. Implementar una electrónica compatible con los componentes
actuales disponibles. 2. Proponer una solución completa al problema. 3.
Considerar diseños modulares que permitan adaptarse a parámetros
futuros.

Requerimientos específicos
~~~~~~~~~~~~~~~~~~~~~~~~~~

A continuación se enlista un set de requerimientos específicos del
proyecto: 1. Los LEDs azules empleados para iluminar la muestra
corresponden a los `Super Bright 5mm
Blue <https://www.superbrightleds.com/moreinfo/through-hole/5mm-blue-led-120-degree-viewing-angle-flat-tipped-1200-mcd/265/1192/>`__:
\* Longitud de onda: 470nm \* Forward current: 30mA @ 3.3V \* Peak
forward current: 100mA \* Max voltage forward: 3.8V

2. Actualmente, se está pensando en una placa de LEDs azules con
   distribución física del tipo circular. Esto implicaría una cantidad
   de 55 LEDs. En la siguiente imagen se muestra esta topología
   propuesta:

Propuesta nueva disposición LEDs azules

   Propuesta nueva disposición LEDs azules

3. Los LEDs verdes empleados para la activación de genes corresponden a
   los `Kingbright
   WP7083ZGD/G <http://www.kingbrightusa.com/images/catalog/SPEC/WP7083ZGD-G.pdf>`__:

   -  Longitud de onda: 520nm
   -  Forward current (typ): 20mA @ 3.2V
   -  Peak forward current: 100mA
   -  Max voltage forward: 4V

4. Los LEDs rojos empleados para la desactivación de genes corresponden
   a los `Deep-Red 5mm
   LED <https://www.ledsupply.com/leds/5mm-led-deep-red-660nm-50-degree-viewing-angle>`__:

   -  Longitud de onda: 660nm
   -  Forward current (typ): 20mA @ 2.2V
   -  Peak forward current: 100mA
   -  Max voltage forward: 2.8V

5. Los LEDs blancos se implementan por medio de una tira LED comercial.
   Típicamente su operación se caracteriza por:

   -  Forward current: 20mA @ 12V

6. El control implementado debe corresponder a PWM, con el fin de
   regular la intensidad lumínica de los LEDs. Se opta por este control
   debido a su sencilla implementación.

7. El sistema debe contar con un sistema de distribución de potencia
   para alimentar todos los sub-módulos, LEDs y raspberry.

8. El sistema debe contar, además, con la posibilidad de leer sensores
   que permitan medir y calibrar la intensidad de luz proveniente desde
   los LEDs. Dado que el control se implementa por medio de una
   raspberry, es necesario utilizar sensores digitales o incluir en el
   diseño un ADC que permita realizar la conversión. En este último caso
   será necesaria la inclusión de una etapa que acondicione las señales
   provenientes desde los sensores.

9. El sensor de intensidad lumínica tiene que cumplir:

-  Bajo costo
-  Fácil de conseguir
-  Respuesta plana para los LED Rojo y Verde

Una alternativa es el fototransistor
`TEMT6000 <https://learn.sparkfun.com/tutorials/temt6000-ambient-light-sensor-hookup-guide/all>`__.

10. El sensor de temperatura es un NTC (termistor).
    `Aquí <https://www.adafruit.com/product/372>`__ se presenta una
    alternativa.

11. El heater es del tipo resistivo y se debe poder alimentar con 9V ó
    12V. Se debe implementar un control PWM de corriente utilizando un
    transistor. Una posible alternativa de heater es el `Film Heating
    Panel <http://www.icstation.com/heating-thin-film-polyimide-heating-plate-panel-25x50mm-b1221-p-9887.html>`__.

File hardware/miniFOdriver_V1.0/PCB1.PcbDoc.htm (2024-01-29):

Reporting Options

# File in Newer Format

Date | : | 02-09-2021
Time | : | 23:33:18
Filename | : | C:\Users\Wac\Desktop\repo_pega\iowlabs\MiniFluOpti\3 - Hardware\miniFOdriver_V1.0\PCB1.PcbDoc

Version | Warning
Release 20.0 | CAUTION - Support of propagation delay for primitives
Release 20.0 | CAUTION - Support for PCB system parameters, used to contain additional data extracted from components

This file was generated by a later version of the software

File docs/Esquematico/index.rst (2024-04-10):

Esquemático
-----------

En la siguiente figura se muestra el diagrama de bloques del esquemático
implementado

Diagrama de bloques del esquemático

   Diagrama de bloques del esquemático

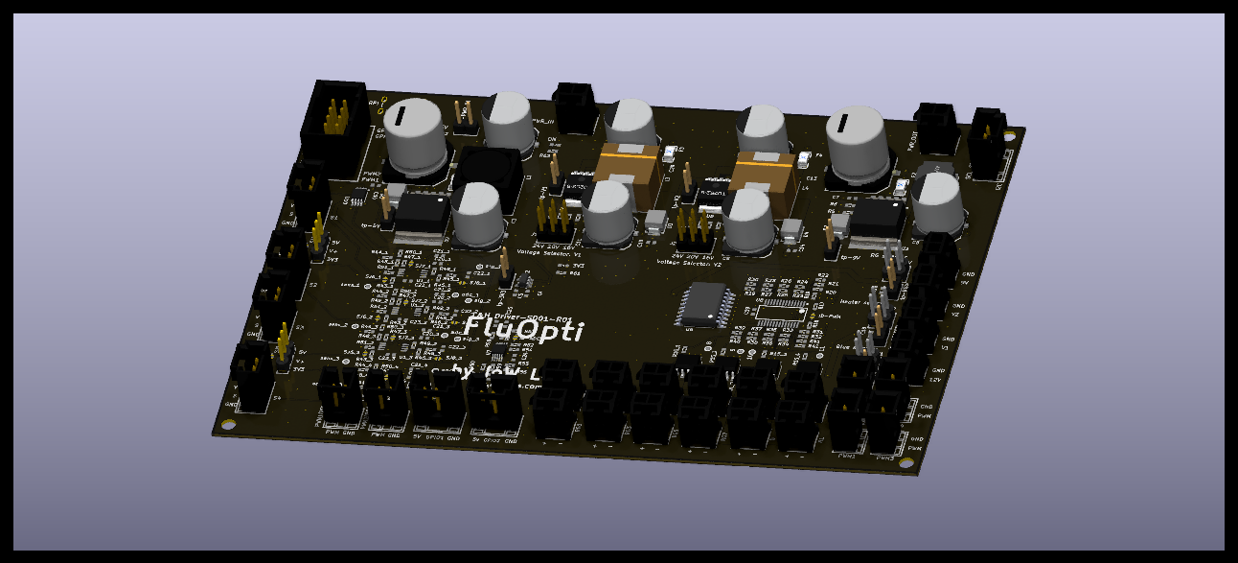
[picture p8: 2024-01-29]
hardware/FOdriver_V2.0/PCBV2.png

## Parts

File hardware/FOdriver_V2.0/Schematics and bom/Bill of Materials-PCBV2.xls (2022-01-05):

Comment | Description | Designator | Footprint | Quantity | Supplier Part Number 1 | Value
TP | Solder test point | 0, 1, 2, 3, 4, 5, 6, 7, 8, 9, 10, 11, 12, 13, 14, 15, adc_1, adc_2, adc_3, adc_4, sens_1, sens_2, sens_3, sens_4, sig_1, sig_2, sig_3, sig_4 | TP | 28
Generic LED | Generic LED SMD | 3V3, 5V, ON | LED0603 | 3 | C125101 (https://octopart-clicks.com/click/altium?manufacturer=Vishay%20Lite-On&mpn=LTST-C191TGKT&seller=LCSC&sku=C125101&country=CL&channel=BOM%20Report)
Power connector 2x1 | Generic Header Power 2pos | 9V, 12V, B, H1, H2, PWR_IN, PWR_OUT, RG1, RG2, RG3, RG4, RG5, RG6, RG7, RG8, V1, V2, W | CONN-TH_430450212 | 18 | C293362 (https://octopart-clicks.com/click/altium?manufacturer=Molex&mpn=43045-0212&seller=LCSC&sku=C293362&country=CL&channel=BOM%20Report)
Pin Header 2x2c | Pin Header 4pos, 2 row, 2.54 pitch | Blue selector, Heater selector, RG selector | HDR-TH_4P-P2.54-V-R2-C2-S2.54_A2541WV-2X2P | 3 | C225517 (https://octopart-clicks.com/click/altium?manufacturer=Loading...&mpn=Loading...&seller=LCSC&sku=C225517&country=CL&channel=BOM%20Report)
Cap pol | Electrolytic Aluminium Capacitor | C1, C12, C15 | CAP_SMD_Electrolytic_10x10 | 3 | C249662 (https://octopart-clicks.com/click/altium?manufacturer=Loading...&mpn=Loading...&seller=LCSC&sku=C249662&country=CL&channel=BOM%20Report) | 47uF
Cap pol | Electrolytic Aluminium Capacitor | C2, C6 | CAP_SMD_Electrolytic_13.5x13.5 | 2 | C178568 (https://octopart-clicks.com/click/altium?manufacturer=Panasonic&mpn=EEE-FK1V681AQ&seller=LCSC&sku=C178568&country=CL&channel=BOM%20Report) | 680uF
Cap pol | Electrolytic Aluminium Capacitor | C3, C8 | CAP_SMD_Electrolytic_10x10 | 2 | C336488 (https://octopart-clicks.com/click/altium?manufacturer=Panasonic&mpn=EEE-1VA331UAP&seller=LCSC&sku=C336488&country=CL&channel=BOM%20Report) | 330uF
Cap Semi | Capacitor (Semiconductor SIM Model) | C4, C5 | 1608[0603] | 2 | C59782 (https://octopart-clicks.com/click/altium?manufacturer=Samsung&mpn=CL10B105KO8NNNC&seller=LCSC&sku=C59782&country=CL&channel=BOM%20Report) | 1uF
Cap Semi | Capacitor (Semiconductor SIM Model) | C7 | 1608[0603] | 1 | C152947 (https://octopart-clicks.com/click/altium?manufacturer=Loading...&mpn=Loading...&seller=LCSC&sku=C152947&country=CL&channel=BOM%20Report) | 1.5nF
Cap pol | Electrolytic Aluminium Capacitor | C9, C11 | CAP_SMD_Electrolytic_10x10 | 2 | C134732 (https://octopart-clicks.com/click/altium?manufacturer=Loading...&mpn=Loading...&seller=LCSC&sku=C134732&country=CL&channel=BOM%20Report) | 220uF
Cap Semi | Capacitor (Semiconductor SIM Model) | C10, C13, C14, C16, C17, C18, C29 | 1608[0603] | 7 | C15849 (https://octopart-clicks.com/click/altium?manufacturer=Samsung&mpn=CL10A105KB8NNNC&seller=LCSC&sku=C15849&country=CL&channel=BOM%20Report) | 1uF
Cap Semi | Capacitor (Semiconductor SIM Model) | C19, C20_1, C20_2, C20_3, C20_4 | 1608[0603] | 5 | C1691 (https://octopart-clicks.com/click/altium?manufacturer=Samsung&mpn=CL10A106MQ8NNNC&seller=LCSC&sku=C1691&country=CL&channel=BOM%20Report) | 10uF
Cap Semi | Capacitor (Semiconductor SIM Model) | C21_1, C21_2, C21_3, C21_4, C22_1, C22_2, C22_3, C22_4, C23_1, C23_2, C23_3, C23_4 | 1608[0603] | 12 | C519410 (https://octopart-clicks.com/click/altium?manufacturer=Loading...&mpn=Loading...&seller=LCSC&sku=C519410&country=CL&channel=BOM%20Report) | 100pF
Cap Semi | Capacitor (Semiconductor SIM Model) | C24, C25, C26, C27, C28, C30 | 1608[0603] | 6 | C386152 (https://octopart-clicks.com/click/altium?manufacturer=Taiyo%20Yuden&mpn=UMK107B104KAHT&seller=LCSC&sku=C386152&country=CL&channel=BOM%20Report) | 100nF
Schottky Diode | Schottky Diodes | D1, D2, D3, D4 | SMB_L4.6-W3.6-LS5.3-RD | 4 | C139945 (https://octopart-clicks.com/click/altium?manufacturer=MCC&mpn=SK32B-LTP&seller=LCSC&sku=C139945&country=CL&channel=BOM%20Report)
Generic Fuse | SMD Fuse | F1, F2, F3, F4 | F1206 | 4 | C310980 (https://octopart-clicks.com/click/altium?manufacturer=Loading...&mpn=Loading...&seller=LCSC&sku=C310980&country=CL&channel=BOM%20Report)
Generic Header 3x1 | Generic Header 3pos, 1 row, 2.54 pitch | GPIO1, GPIO2, I2C, S1, S2, S3, S4 | CONN-TH_A2547WV-3P | 7 | C239378 (https://octopart-clicks.com/click/altium?manufacturer=CJT%20Connectors&mpn=A2547WV-3P&seller=LCSC&sku=C239378&country=CL&channel=BOM%20Report)
sj | solder jumper generic | ID-ADC, ID-PWM, SJ1, SJ2, SJ3, SJ4, SJ6_1, SJ6_2, SJ6_3, SJ6_4, SJ7_1, SJ7_2, SJ7_3, SJ7_4, SJ8_1, SJ8_2, SJ8_3, SJ8_4 | SJ2 | 18
Pin Header 3x2 | Pin Header 6pos, 2 row, 2.54 pitch | J1, J2 | HDR-TH_6P-P2.54-V-R2-C3-S2.54_A2541WV-2X3P | 2 | C225518 (https://octopart-clicks.com/click/altium?manufacturer=Loading...&mpn=Loading...&seller=LCSC&sku=C225518&country=CL&channel=BOM%20Report)
Pin Header 3x1 | Pin Header 3pos, 1 row, 2.54 pitch | L, T | HDR-TH_3P-P2.54-V | 2 | C225478 (https://octopart-clicks.com/click/altium?manufacturer=Loading...&mpn=Loading...&seller=LCSC&sku=C225478&country=CL&channel=BOM%20Report)
Inductor | Inductor SMD | L1 | IND-SMD_L12.5-W12.5_SMDRS1275 | 1 | C238002 (https://octopart-clicks.com/click/altium?manufacturer=Loading...&mpn=Loading...&seller=LCSC&sku=C238002&country=CL&channel=BOM%20Report) | 68uH
Inductor | Inductor SMD | L2 | IND-SMD_L8.0-W8.0 | 1 | C280555 (https://octopart-clicks.com/click/altium?manufacturer=Loading...&mpn=Loading...&seller=LCSC&sku=C280555&country=CL&channel=BOM%20Report) | 15uH
Inductor | Inductor SMD | L3, L4 | IND-SMD_L12.3-W12.3 | 2 | C9400 (https://octopart-clicks.com/click/altium?manufacturer=Loading...&mpn=Loading...&seller=LCSC&sku=C9400&country=CL&channel=BOM%20Report) | 33uH
Generic header 2x1 | Generic Header 2pos, 1 row, 2.54 pitch | PWM1, PWM1(RPI), PWM2, PWM2(RPI), PWM3, PWM4 | CONN-TH_A2547WV-2P | 6 | C239377 (https://octopart-clicks.com/click/altium?manufacturer=Loading...&mpn=Loading...&seller=LCSC&sku=C239377&country=CL&channel=BOM%20Report)
USB-C female 6 | USB - Type C Female 6 USB Connectors RoHS | PWR_RPI | USB-C_SMD 6 contacts | 1 | C283540 (https://octopart-clicks.com/click/altium?manufacturer=HRO%20Electronics&mpn=TYPE-C-31-M-17&seller=LCSC&sku=C283540&country=CL&channel=BOM%20Report)
IRF7401PbF-1 | MOSFET N Channel 20V 8.7A 700mV @ 250uA 22mO @ 4.1A,4.5V SOIC-8_150mil RoHS | Q1_1, Q1_2, Q1_3, Q1_4 | SOIC8 | 4 | C169092 (https://octopart-clicks.com/click/altium?manufacturer=Infineon&mpn=IRF7401TRPBF&seller=LCSC&sku=C169092&country=CL&channel=BOM%20Report)
Res3 | Resistor | R1, R2, R3, R4, R16_1, R16_2, R16_3, R16_4, R18, R19, R41, R42, R53, R55, R56 | J1-0603 | 15 | C161787 (https://octopart-clicks.com/click/altium?manufacturer=Panasonic&mpn=ERJ-PB3B1002V&seller=LCSC&sku=C161787&country=CL&channel=BOM%20Report) | 10K
Res3 | Resistor | R5, R7, R11 | J1-0603 | 3 | C323557 (https://octopart-clicks.com/click/altium?manufacturer=Loading...&mpn=Loading...&seller=LCSC&sku=C323557&country=CL&channel=BOM%20Report) | 1K
Res3 | Resistor | R6 | J1-0603 | 1 | C185314 (https://octopart-clicks.com/click/altium?manufacturer=Loading...&mpn=Loading...&seller=LCSC&sku=C185314&country=CL&channel=BOM%20Report) | 6.34K
Res3 | Resistor | R8, R12 | J1-0603 | 2 | C227561 (https://octopart-clicks.com/click/altium?manufacturer=Loading...&mpn=Loading...&seller=LCSC&sku=C227561&country=CL&channel=BOM%20Report) | 11.8K
Res3 | Resistor | R9, R13 | J1-0603 | 2 | C114661 (https://octopart-clicks.com/click/altium?manufacturer=Loading...&mpn=Loading...&seller=LCSC&sku=C114661&country=CL&channel=BOM%20Report) | 15K
Res3 | Resistor | R10, R14 | J1-0603 | 2 | C103358 (https://octopart-clicks.com/click/altium?manufacturer=Loading...&mpn=Loading...&seller=LCSC&sku=C103358&country=CL&channel=BOM%20Report) | 18.2K
Res3 | Resistor | R15_1, R15_2, R15_3, R15_4 | J1-0603 | 4 | C308180 (https://octopart-clicks.com/click/altium?manufacturer=Rohm&mpn=MCR03EZPFX1100&seller=LCSC&sku=C308180&country=CL&channel=BOM%20Report) | 110
Res3 | Resistor | R17, R20, R21, R22, R31, R32, R52, R54 | J1-0603 | 8 | C105576 (https://octopart-clicks.com/click/altium?manufacturer=Loading...&mpn=Loading...&seller=LCSC&sku=C105576&country=CL&channel=BOM%20Report) | 2K
Res3 | Resistor | R23, R24, R25, R26, R27, R28, R29, R30, R33, R34, R35, R36, R37, R38, R39, R40, R57, R58, R59, R60 | J1-0603 | 20 | C107696 (https://octopart-clicks.com/click/altium?manufacturer=Loading...&mpn=Loading...&seller=LCSC&sku=C107696&country=CL&channel=BOM%20Report) | 220
Res3 | Resistor | R43_1, R43_2, R43_3, R43_4, R47_1, R47_2, R47_3, R47_4, R48_1, R48_2, R48_3, R48_4, R51_1, R51_2, R51_3, R51_4 | J1-0603 | 16 | C380376 (https://octopart-clicks.com/click/altium?manufacturer=Rohm&mpn=MCR03EZPFX1201&seller=LCSC&sku=C380376&country=CL&channel=BOM%20Report) | 1.2K
Res3 | Resistor | R44_1, R44_2, R44_3, R44_4, R45_1, R45_2, R45_3, R45_4, R46_1, R46_2, R46_3, R46_4, R50_1, R50_2, R50_3, R50_4 | J1-0603 | 16 | C114662 (https://octopart-clicks.com/click/altium?manufacturer=Loading...&mpn=Loading...&seller=LCSC&sku=C114662&country=CL&channel=BOM%20Report) | 2.2K
Res3 | Resistor | R49_1, R49_2, R49_3, R49_4, R62 | J1-0603 | 5 | C105588 (https://octopart-clicks.com/click/altium?manufacturer=Loading...&mpn=Loading...&seller=LCSC&sku=C105588&country=CL&channel=BOM%20Report) | 100
Res3 | Resistor | R61 | J1-0603 | 1 | C109318 (https://octopart-clicks.com/click/altium?manufacturer=Loading...&mpn=Loading...&seller=LCSC&sku=C109318&country=CL&channel=BOM%20Report) | 10
Res3 | Resistor | R63 | J1-0603 | 1 | C227905 (https://octopart-clicks.com/click/altium?manufacturer=Loading...&mpn=Loading...&seller=LCSC&sku=C227905&country=CL&channel=BOM%20Report) | 442
Generic Header 4x2 | Generic Header 8 pos, 2 row, 2.54 pitch | RPI_IN | CONN-TH_8P-P2.54-V-M_15477608 | 1 | C277394 (https://octopart-clicks.com/click/altium?manufacturer=Molex&mpn=15-47-7608&seller=LCSC&sku=C277394&country=CL&channel=BOM%20Report)
Pin Header 2x1 | Pin Header 2pos, 1 row, 2.54 pitch | tp-3V3, tp-5V, tp-9V, tp-BLUE>, tp-HEATER>, tp-PWR_IN, tp-RG>, tp-V1, tp-V2 | HDR-TH_P2.54-H-M_A2541WV-2P | 9 | C225477 (https://octopart-clicks.com/click/altium?manufacturer=Loading...&mpn=Loading...&seller=LCSC&sku=C225477&country=CL&channel=BOM%20Report)
OPA2333AIDGKR | Precision OpAmps Zero-Drift 2 1.8V ~ 5.5V, ±0.9V ~ 2.75V 350kHz 0.16 V/us MSOP-8 RoHS | U1_1, U1_2, U1_3, U1_4 | MSOP-8 | 4 | C19608 (https://octopart-clicks.com/click/altium?manufacturer=Texas%20Instruments&mpn=OPA2333AIDGKR&seller=LCSC&sku=C19608&country=CL&channel=BOM%20Report)
AP2112K-3.3TRG1 | 600mA CMOS LDO REGULATOR WITH ENABLE | U2 | SOT25-5 | 1 | C51118 (https://octopart-clicks.com/click/altium?manufacturer=Diodes&mpn=AP2112K-3.3TRG1&seller=LCSC&sku=C51118&country=CL&channel=BOM%20Report)
LM2596-ADJ | DC-DC Converters Step-Down Adjustable 1 4.5V 40V 1.2V 37V 3A TO-263-5 RoHS | U3 | TO-263-5 | 1 | C29781 (https://octopart-clicks.com/click/altium?manufacturer=TI%20National%20Semiconductor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)
XL6008 | DC-DC Converters Step-Up, Step-Up/Step-Down Adjustable 1 3.6V 32V 3A TO-252-5 RoHS | U4, U5 | TO-252-5 | 2 | C73012 (https://octopart-clicks.com/click/altium?manufacturer=Loading...&mpn=Loading...&seller=LCSC&sku=C73012&country=CL&channel=BOM%20Report)
ULN2803A | Darlington transistor array driver SOIC-18_300mi | U6 | SOIC18 | 1 | C9683 (https://octopart-clicks.com/click/altium?manufacturer=Texas%20Instruments&mpn=ULN2803ADWR&seller=LCSC&sku=C9683&country=CL&channel=BOM%20Report)
ADS1115 | Analog To Digital Converters (ADCs) VSSOP-10 RoHS | U7 | VSSOP - 10 | 1 | C172375 (https://octopart-clicks.com/click/altium?manufacturer=Texas%20Instruments&mpn=ADS1115QDGSRQ1&seller=LCSC&sku=C172375&country=CL&channel=BOM%20Report)
PCA9685 | LED Drivers,16CH, I2C, TSSOP-28 | U8 | SSOP-28_L | 1 | C92206 (https://octopart-clicks.com/click/altium?manufacturer=NXP%20Semiconductors&mpn=PCA9685PW%2FQ900%2C118&seller=LCSC&sku=C92206&country=CL&channel=BOM%20Report)
LM2596-5V | Step-Down Positive Fixed 1 3A 150kHz TO-263-5 DC-DC Converters RoHS | U9 | TO-263-5 | 1 | C77782 (https://octopart-clicks.com/click/altium?manufacturer=Loading...&mpn=Loading...&seller=LCSC&sku=C77782&country=CL&channel=BOM%20Report)
TCA9517A | VSSOP-8_3x3x065P Level Translators, Shifters RoHS | U10 | VSSOP - 8 | 1 | C201698 (https://octopart-clicks.com/click/altium?manufacturer=Loading...&mpn=Loading...&seller=LCSC&sku=C201698&country=CL&channel=BOM%20Report)

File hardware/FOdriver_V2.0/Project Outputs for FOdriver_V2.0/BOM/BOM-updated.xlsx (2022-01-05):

Comment | Description | Designator | Quantity per PCB | Total Quantity | Manufacturer | Supplier Part Number 1 | # PCB | 2
OPA2333AIDGKR | Precision OpAmps Zero-Drift 2 1.8V ~ 5.5V, ±0.9V ~ 2.75V 350kHz 0.16 V/us MSOP-8 RoHS | U1_1, U1_2, U1_3, U1_4 | 4 | 8 | Texas Instruments | C19608 (https://octopart-clicks.com/click/altium?manufacturer=Texas%20Instruments&mpn=OPA2333AIDGKR&seller=LCSC&sku=C19608&country=CL&channel=BOM%20Report)
Power connector 2x1 | Generic Header Power 2pos | 9V, 12V, B, H1, H2, PWR_IN, PWR_OUT, RG1, RG2, RG3, RG4, RG5, RG6, RG7, RG8, V1, V2, W | 18 | 36 | MOLEX | C293362 (https://octopart-clicks.com/click/altium?manufacturer=Molex&mpn=0430450212&seller=LCSC&sku=C293362&country=CL&channel=BOM%20Report)
LM2596-ADJ | DC-DC Converters Step-Down Adjustable 1 4.5V 40V 1.2V 37V 3A TO-263-5 RoHS | U3 | 1 | 2 | Texas Instruments | C29781 (https://octopart-clicks.com/click/altium?manufacturer=TI%20National%20Semiconductor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)
IRF7401PbF-1 | MOSFET N Channel 20V 8.7A 700mV @ 250uA 22mΩ @ 4.1A,4.5V SOIC-8_150mil RoHS | Q1_1, Q1_2, Q1_3, Q1_4 | 4 | 8 | Infineon Technologies | C169092 (https://octopart-clicks.com/click/altium?manufacturer=Infineon&mpn=IRF7401TRPBF&seller=LCSC&sku=C169092&country=CL&channel=BOM%20Report)
Generic Header 4x2 | Generic Header 8 pos, 2 row, 2.54 pitch | RPI_IN | 1 | 2 | MOLEX | C277394 (https://octopart-clicks.com/click/altium?manufacturer=Molex&mpn=15-47-7608&seller=LCSC&sku=C277394&country=CL&channel=BOM%20Report)
ULN2803A | Darlington transistor array driver SOIC-18_300mi | U6 | 1 | 2 | Texas instrument | C9683 (https://octopart-clicks.com/click/altium?manufacturer=Texas%20Instruments&mpn=ULN2803ADWR&seller=LCSC&sku=C9683&country=CL&channel=BOM%20Report)
USB-C female 6 | USB - Type C Female 6 USB Connectors RoHS | PWR_RPI | 1 | 2 | Korean Hroparts Elec | C283540 (https://octopart-clicks.com/click/altium?manufacturer=HRO%20Electronics&mpn=TYPE-C-31-M-17&seller=LCSC&sku=C283540&country=CL&channel=BOM%20Report)
AP2112K-3.3TRG1 | 600mA CMOS LDO REGULATOR WITH ENABLE | U2 | 1 | 2 | DIODES | C51118 (https://octopart-clicks.com/click/altium?manufacturer=Diodes&mpn=AP2112K-3.3TRG1&seller=LCSC&sku=C51118&country=CL&channel=BOM%20Report)
ADS1115 | Analog To Digital Converters (ADCs) VSSOP-10 RoHS | U7 | 1 | 2 | Texas Instruments | C172375 (https://octopart-clicks.com/click/altium?manufacturer=Texas%20Instruments&mpn=ADS1115QDGSRQ1&seller=LCSC&sku=C172375&country=CL&channel=BOM%20Report)
Cap pol | Electrolytic Aluminium Capacitor | C1, C12, C15 | 3 | 6 | Lelon | C249662 (https://octopart-clicks.com/click/altium?manufacturer=Loading...&mpn=Loading...&seller=LCSC&sku=C249662&country=CL&channel=BOM%20Report)
Cap pol | Electrolytic Aluminium Capacitor | C2, C6 | 2 | 4 | PANASONIC | C178568 (https://octopart-clicks.com/click/altium?manufacturer=Panasonic&mpn=EEE-FK1V681AQ&seller=LCSC&sku=C178568&country=CL&channel=BOM%20Report)
Cap pol | Electrolytic Aluminium Capacitor | C3, C8 | 2 | 4 | PANASONIC | C336488 (https://octopart-clicks.com/click/altium?manufacturer=Panasonic&mpn=EEE-1VA331UAP&seller=LCSC&sku=C336488&country=CL&channel=BOM%20Report)
Cap pol | Electrolytic Aluminium Capacitor | C9, C11 | 2 | 4 | Lelon | C134732 (https://octopart-clicks.com/click/altium?manufacturer=Loading...&mpn=Loading...&seller=LCSC&sku=C134732&country=CL&channel=BOM%20Report)
Cap Semi | Capacitor (Semiconductor SIM Model) | C10, C13, C14, C16, C17, C18, C29 | 7 | 14 | Samsung Electro-Mechanics | C15849 (https://octopart-clicks.com/click/altium?manufacturer=Samsung&mpn=CL10A105KB8NNNC&seller=LCSC&sku=C15849&country=CL&channel=BOM%20Report)
Cap Semi | Capacitor (Semiconductor SIM Model) | C19, C20_1, C20_2, C20_3, C20_4 | 5 | 10 | Samsung Electro-Mechanics | C1691 (https://octopart-clicks.com/click/altium?manufacturer=Samsung&mpn=CL10A106MQ8NNNC&seller=LCSC&sku=C1691&country=CL&channel=BOM%20Report)
Cap Semi | Capacitor (Semiconductor SIM Model) | C21_1, C21_2, C21_3, C21_4, C22_1, C22_2, C22_3, C22_4, C23_1, C23_2, C23_3, C23_4 | 12 | 24 | YAGEO | C160903 (https://octopart-clicks.com/click/altium?manufacturer=Loading...&mpn=Loading...&seller=LCSC&sku=C160903&country=CL&channel=BOM%20Report)
Cap Semi | Capacitor (Semiconductor SIM Model) | C24, C25, C26, C27, C28, C30 | 6 | 12 | Taiyo Yuden | C386152 (https://octopart-clicks.com/click/altium?manufacturer=Loading...&mpn=Loading...&seller=LCSC&sku=C386152&country=CL&channel=BOM%20Report)
Cap Semi | Capacitor (Semiconductor SIM Model) | C4, C5 | 2 | 4 | Samsung Electro-Mechanics | C59782 (https://octopart-clicks.com/click/altium?manufacturer=Samsung&mpn=CL10B105KO8NNNC&seller=LCSC&sku=C59782&country=CL&channel=BOM%20Report)
Cap Semi | Capacitor (Semiconductor SIM Model) | C7 | 1 | 2 | Walsin Tech Corp | C152947 (https://octopart-clicks.com/click/altium?manufacturer=Loading...&mpn=Loading...&seller=LCSC&sku=C152947&country=CL&channel=BOM%20Report)
Generic Fuse | SMD Fuse | F1, F2, F3, F4 | 4 | 8 | AEM | C310980 (https://octopart-clicks.com/click/altium?manufacturer=Loading...&mpn=Loading...&seller=LCSC&sku=C310980&country=CL&channel=BOM%20Report)
Generic header 2x1 | Generic Header 2pos, 1 row, 2.54 pitch | PWM1, PWM1(RPI), PWM2, PWM2(RPI), PWM3, PWM4 | 6 | 12 | CJT(Changjiang Connectors) | C239377 (https://octopart-clicks.com/click/altium?manufacturer=Loading...&mpn=Loading...&seller=LCSC&sku=C239377&country=CL&channel=BOM%20Report)
Generic Header 3x1 | Generic Header 3pos, 1 row, 2.54 pitch | GPIO1, GPIO2, I2C, S1, S2, S3, S4 | 7 | 14 | CJT(Changjiang Connectors) | C239378 (https://octopart-clicks.com/click/altium?manufacturer=Loading...&mpn=Loading...&seller=LCSC&sku=C239378&country=CL&channel=BOM%20Report)
Generic LED | Generic LED SMD | 3V3, 5V, ON | 3 | 6 | Lite-On | C125101 (https://octopart-clicks.com/click/altium?manufacturer=Vishay%20Lite-On&mpn=LTST-C191TGKT&seller=LCSC&sku=C125101&country=CL&channel=BOM%20Report)
Inductor | Inductor SMD | L1 | 1 | 2 | GLE | C439422 (https://octopart-clicks.com/click/altium?manufacturer=Loading...&mpn=Loading...&seller=LCSC&sku=C439422&country=CL&channel=BOM%20Report)
Inductor | Inductor SMD | L2 | 1 | 2 | 3L COILS | C326353 (https://octopart-clicks.com/click/altium?manufacturer=Loading...&mpn=Loading...&seller=LCSC&sku=C326353&country=CL&channel=BOM%20Report)
Inductor | Inductor SMD | L3, L4 | 2 | 4 | SXN(Shun Xiang Nuo Elec) | C9400 (https://octopart-clicks.com/click/altium?manufacturer=Loading...&mpn=Loading...&seller=LCSC&sku=C9400&country=CL&channel=BOM%20Report)
LM2596-5V | Step-Down Positive Fixed 1 3A 150kHz TO-263-5 DC-DC Converters RoHS | U9 | 1 | 2 | HTC Korea TAEJIN Tech | C77782 (https://octopart-clicks.com/click/altium?manufacturer=Loading...&mpn=Loading...&seller=LCSC&sku=C77782&country=CL&channel=BOM%20Report)
PCA9685 | LED Drivers,16CH, I2C, TSSOP-28 | U8 | 1 | 2 | NXP Semicon | C92206 (https://octopart-clicks.com/click/altium?manufacturer=NXP%20Semiconductors&mpn=PCA9685PW%2FQ900%2C118&seller=LCSC&sku=C92206&country=CL&channel=BOM%20Report)
Pin Header 2x1 | Pin Header 2pos, 1 row, 2.54 pitch | tp-3V3, tp-5V, tp-9V, tp-BLUE>, tp-HEATER>, tp-PWR_IN, tp-RG>, tp-V1, tp-V2 | 9 | 18 | CJT(Changjiang Connectors) | C225477 (https://octopart-clicks.com/click/altium?manufacturer=Changjiang%20Electronics&mpn=A2541WV-2P&seller=LCSC&sku=C225477&country=CL&channel=BOM%20Report)
Pin Header 2x2c | Pin Header 4pos, 2 row, 2.54 pitch | Blue selector, Heater selector, RG selector | 3 | 6 | CJT(Changjiang Connectors) | C225517 (https://octopart-clicks.com/click/altium?manufacturer=Loading...&mpn=Loading...&seller=LCSC&sku=C225517&country=CL&channel=BOM%20Report)
Pin Header 3x1 | Pin Header 3pos, 1 row, 2.54 pitch | L, T | 2 | 4 | CJT(Changjiang Connectors) | C225478 (https://octopart-clicks.com/click/altium?manufacturer=Loading...&mpn=Loading...&seller=LCSC&sku=C225478&country=CL&channel=BOM%20Report)
Pin Header 3x2 | Pin Header 6pos, 2 row, 2.54 pitch | J1, J2 | 2 | 4 | CJT(Changjiang Connectors) | C225518 (https://octopart-clicks.com/click/altium?manufacturer=Loading...&mpn=Loading...&seller=LCSC&sku=C225518&country=CL&channel=BOM%20Report)
Res3 | Resistor | R1, R2, R3, R4, R16_1, R16_2, R16_3, R16_4, R18, R19, R41, R42, R53, R55, R56 | 15 | 30 | PANASONIC | C441927 (https://octopart-clicks.com/click/altium?manufacturer=Panasonic&mpn=ERJPA3F1002V&seller=LCSC&sku=C441927&country=CL&channel=BOM%20Report)
Res3 | Resistor | R10, R14 | 2 | 4 | RALEC | C103358 (https://octopart-clicks.com/click/altium?manufacturer=Loading...&mpn=Loading...&seller=LCSC&sku=C103358&country=CL&channel=BOM%20Report)
Res3 | Resistor | R15_1, R15_2, R15_3, R15_4 | 4 | 8 | ROHM Semicon | C308180 (https://octopart-clicks.com/click/altium?manufacturer=Rohm&mpn=MCR03EZPFX1100&seller=LCSC&sku=C308180&country=CL&channel=BOM%20Report)
Res3 | Resistor | R17, R20, R21, R22, R31, R32, R52, R54 | 8 | 16 | YAGEO | C105576 (https://octopart-clicks.com/click/altium?manufacturer=Loading...&mpn=Loading...&seller=LCSC&sku=C105576&country=CL&channel=BOM%20Report)
Res3 | Resistor | R23, R24, R25, R26, R27, R28, R29, R30, R33, R34, R35, R36, R37, R38, R39, R40, R57, R58, R59, R60 | 20 | 40 | YAGEO | C107696 (https://octopart-clicks.com/click/altium?manufacturer=Loading...&mpn=Loading...&seller=LCSC&sku=C107696&country=CL&channel=BOM%20Report)
Res3 | Resistor | R43_1, R43_2, R43_3, R43_4, R47_1, R47_2, R47_3, R47_4, R48_1, R48_2, R48_3, R48_4, R51_1, R51_2, R51_3, R51_4 | 16 | 32 | ROHM Semicon | C380376 (https://octopart-clicks.com/click/altium?manufacturer=Rohm&mpn=MCR03EZPFX1201&seller=LCSC&sku=C380376&country=CL&channel=BOM%20Report)
Res3 | Resistor | R44_1, R44_2, R44_3, R44_4, R45_1, R45_2, R45_3, R45_4, R46_1, R46_2, R46_3, R46_4, R50_1, R50_2, R50_3, R50_4 | 16 | 32 | YAGEO | C114662 (https://octopart-clicks.com/click/altium?manufacturer=Loading...&mpn=Loading...&seller=LCSC&sku=C114662&country=CL&channel=BOM%20Report)
Res3 | Resistor | R49_1, R49_2, R49_3, R49_4, R62 | 5 | 10 | YAGEO | C105588 (https://octopart-clicks.com/click/altium?manufacturer=Loading...&mpn=Loading...&seller=LCSC&sku=C105588&country=CL&channel=BOM%20Report)
Res3 | Resistor | R5, R7, R11 | 3 | 6 | KAMAYA | C323557 (https://octopart-clicks.com/click/altium?manufacturer=Loading...&mpn=Loading...&seller=LCSC&sku=C323557&country=CL&channel=BOM%20Report)
Res3 | Resistor | R6 | 1 | 2 | YAGEO | C185314 (https://octopart-clicks.com/click/altium?manufacturer=Loading...&mpn=Loading...&seller=LCSC&sku=C185314&country=CL&channel=BOM%20Report)
Res3 | Resistor | R61 | 1 | 2 | YAGEO | C109318 (https://octopart-clicks.com/click/altium?manufacturer=Loading...&mpn=Loading...&seller=LCSC&sku=C109318&country=CL&channel=BOM%20Report)
Res3 | Resistor | R63 | 1 | 2 | YAGEO | C227905 (https://octopart-clicks.com/click/altium?manufacturer=Loading...&mpn=Loading...&seller=LCSC&sku=C227905&country=CL&channel=BOM%20Report)
Res3 | Resistor | R8, R12 | 2 | 4 | YAGEO | C227561 (https://octopart-clicks.com/click/altium?manufacturer=Loading...&mpn=Loading...&seller=LCSC&sku=C227561&country=CL&channel=BOM%20Report)
Res3 | Resistor | R9, R13 | 2 | 4 | YAGEO | C114661 (https://octopart-clicks.com/click/altium?manufacturer=Loading...&mpn=Loading...&seller=LCSC&sku=C114661&country=CL&channel=BOM%20Report)
Schottky Diode | Schottky Diodes | D1, D2, D3, D4 | 4 | 8 | MCC(Micro Commercial Components) | C139945 (https://octopart-clicks.com/click/altium?manufacturer=MCC&mpn=SK32B-LTP&seller=LCSC&sku=C139945&country=CL&channel=BOM%20Report)
TCA9517A | VSSOP-8_3x3x065P Level Translators, Shifters RoHS | U10 | 1 | 2 | Texas Instruments | C201698 (https://octopart-clicks.com/click/altium?manufacturer=Loading...&mpn=Loading...&seller=LCSC&sku=C201698&country=CL&channel=BOM%20Report)
XL6008 | DC-DC Converters Step-Up, Step-Up/Step-Down Adjustable 1 3.6V 32V 3A TO-252-5 RoHS | U4, U5 | 2 | 4 | XLSEMI | C73012 (https://octopart-clicks.com/click/altium?manufacturer=Loading...&mpn=Loading...&seller=LCSC&sku=C73012&country=CL&channel=BOM%20Report)
 | Rectangular Connectors Housings RoHS |  | 1 | 2 | MOLEX | C505041
 | Terminals RoHS |  | 8 | 16 | MOLEX | C293377
 | 2 2 0.118"(3.00mm) Male Rectangular Connectors Housings RoHS |  | 18 | 36 | MOLEX | C293523
 | Terminals RoHS |  | 36 | 72 | MOLEX | C259786
 | 3 0.100"(2.54mm) 1 Male P=2.54mm Rectangular Connectors Housings RoHS |  | 7 | 14 | CJT(Changjiang Connectors) | C339379
 | 2 0.100"(2.54mm) 1 Male P=2.54mm Rectangular Connectors Housings RoHS |  | 6 | 12 | CJT(Changjiang Connectors) | C339378
 | Crimping terminal 22~24 RoHS , REACH Terminals RoHS |  | 33 | 66 | CJT(Changjiang Connectors) | C339475
 | P=2.54mm Shunts & Jumpers RoHS |  | 7 | 14 | JST Sales America | C265313

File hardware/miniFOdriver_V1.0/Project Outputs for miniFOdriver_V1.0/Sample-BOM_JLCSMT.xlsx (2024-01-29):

Comment | Designator | Footprint | JLCPCB Part #（optional）
100uF | C1 | CAP-SMD_L3.5-W2.8 | C16133
15K | R5,R6 | R0603 | C22809
DC-005-20A_C136744 | DC1 | DC-IN-TH_DC-005-20A | C136744
Header-Female-2.54_1x8 | P2,P3 | HDR-TH_8P-P2.54-V | C27438
K2-1102DP-C4SW-04 | SW1 | KEY-TH_4P-L6.0-W6.0-P4.50-LS6.5 | C110153
ATMEGA328P-PU | U1 | DIP-28_L34.6-W7.3-P2.54-LS10.2-BL | C33901
670688000 | USB1 | USB-B-TH_67068-8000 | C114097

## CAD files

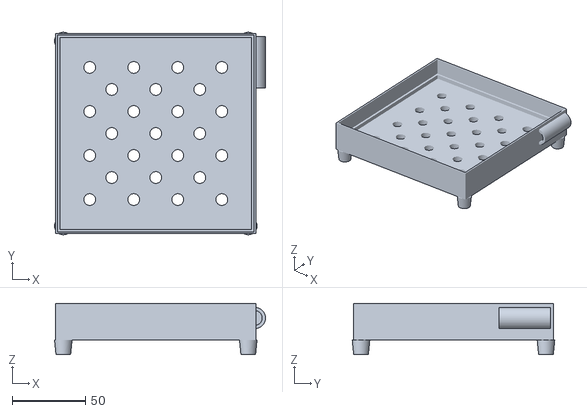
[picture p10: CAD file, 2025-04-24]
3Dmodels/STLs/base_holder.stl
143.8 x 138.0 x 35.0

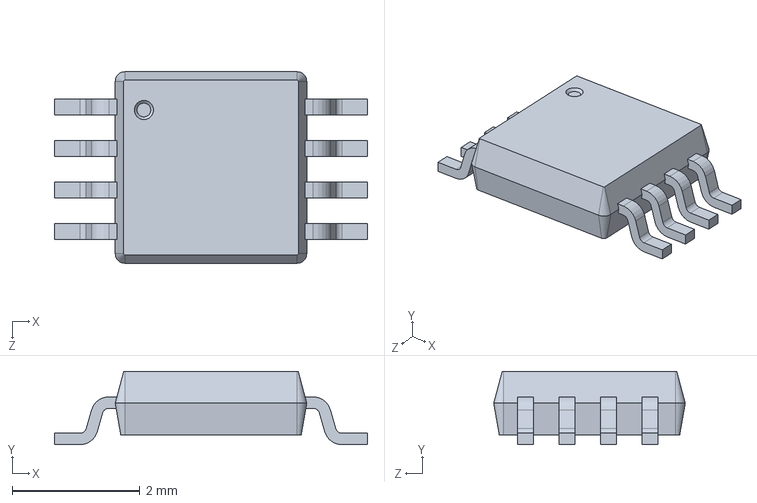
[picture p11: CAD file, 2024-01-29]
hardware/FOdriver_V2.0/ALTIUM_EMBEDDED_MODELS/msop-8.SLDPRT
4.90 x 1.15 x 3.00 mm

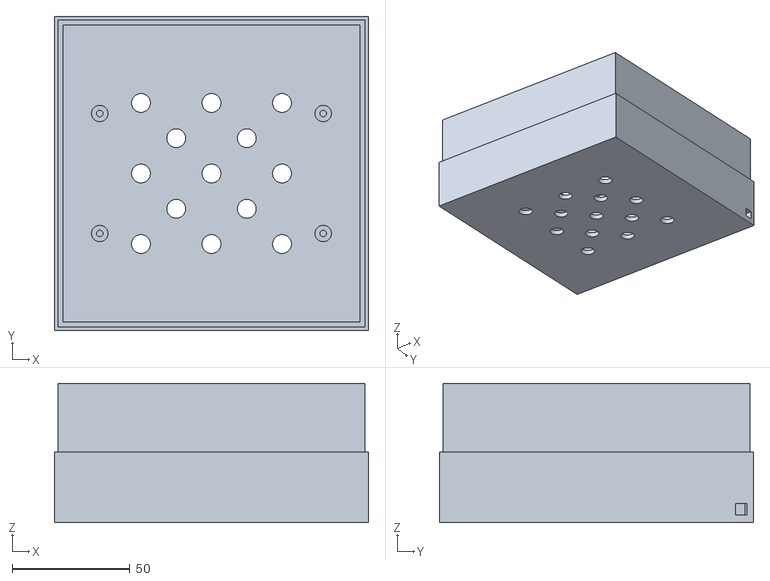
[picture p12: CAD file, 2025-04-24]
3Dmodels/STLs/lighting_base.stl
133.5 x 133.5 x 59.2

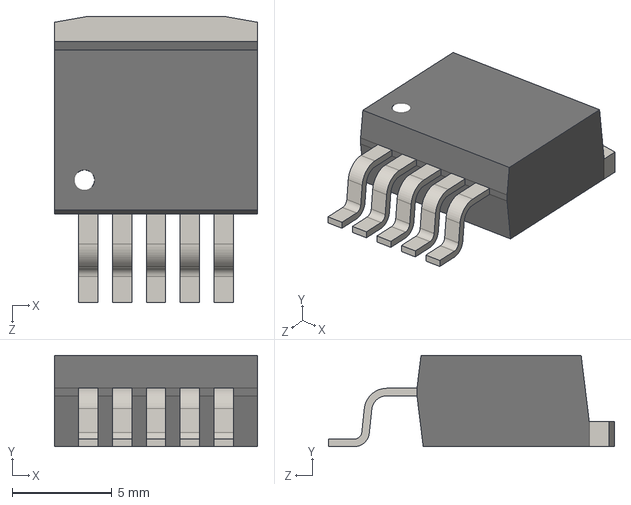
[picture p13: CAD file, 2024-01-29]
hardware/FOdriver_V2.0/ALTIUM_EMBEDDED_MODELS/TS5B.STEP
10.2 x 4.58 x 14.4 mm

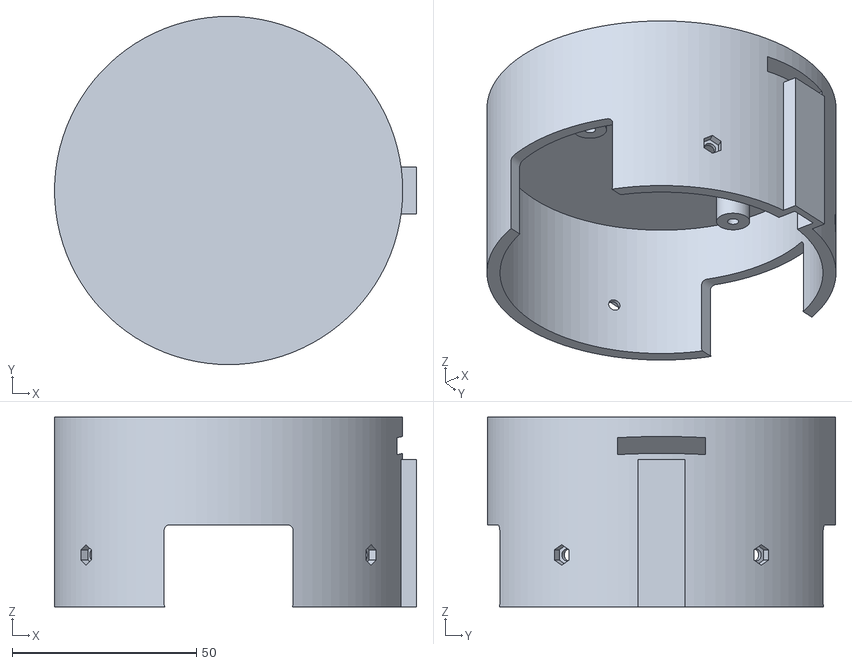
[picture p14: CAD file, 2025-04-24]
3Dmodels/STLs/top_part.stl
98.3 x 94.6 x 51.5

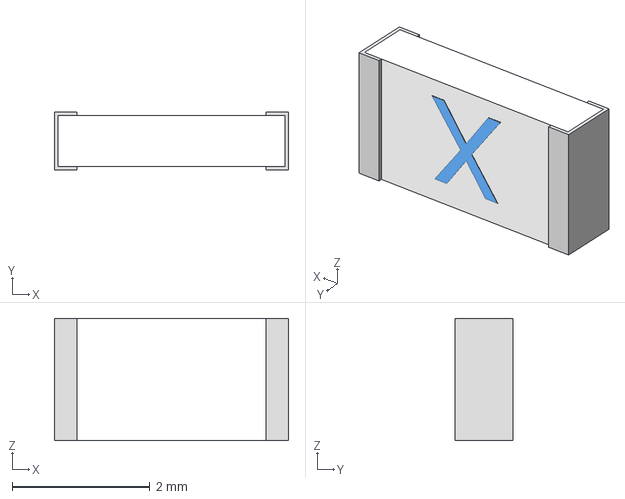
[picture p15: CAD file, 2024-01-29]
hardware/FOdriver_V2.0/ALTIUM_EMBEDDED_MODELS/C1F_Fuse.stp
3.40 x 0.838 x 1.78 mm

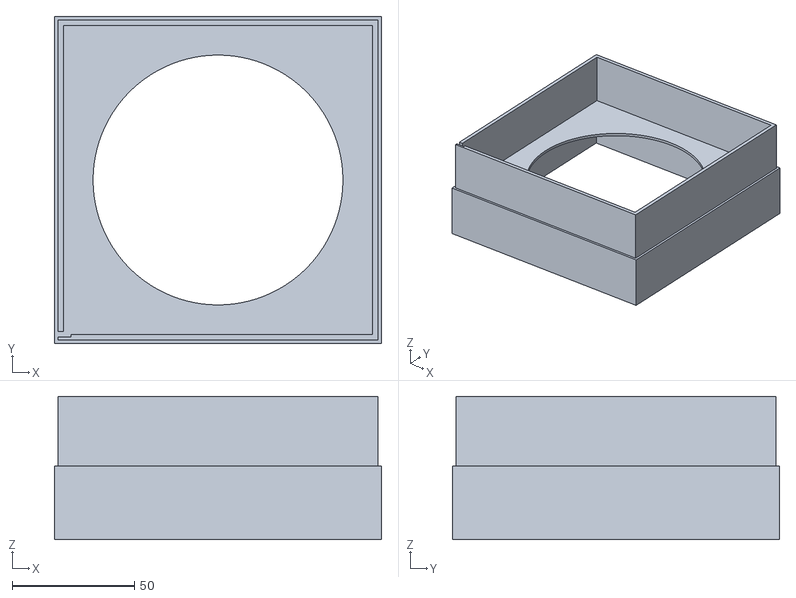
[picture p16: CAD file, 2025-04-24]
3Dmodels/STLs/plate_holder.stl
133.5 x 133.5 x 58.5

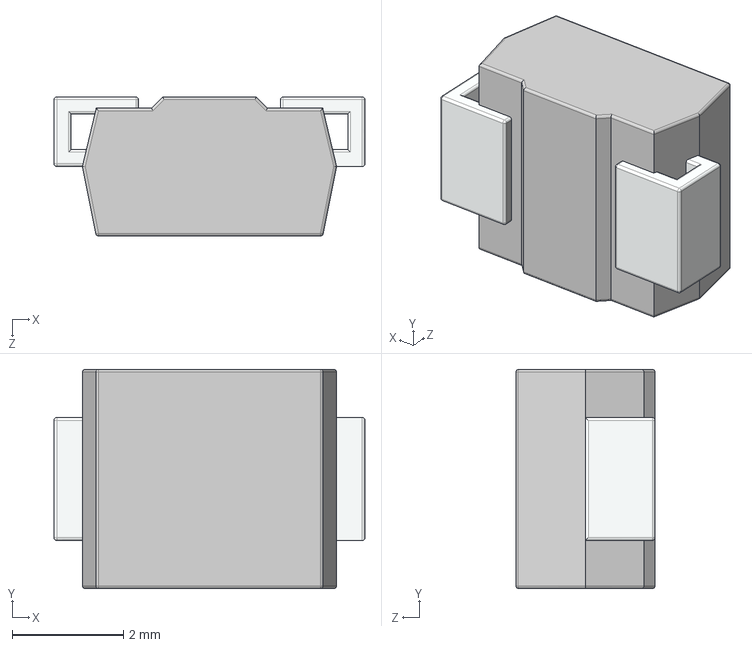
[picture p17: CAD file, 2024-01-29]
hardware/FOdriver_V2.0/ALTIUM_EMBEDDED_MODELS/SMB.STEP
5.59 x 3.94 x 2.50 mm

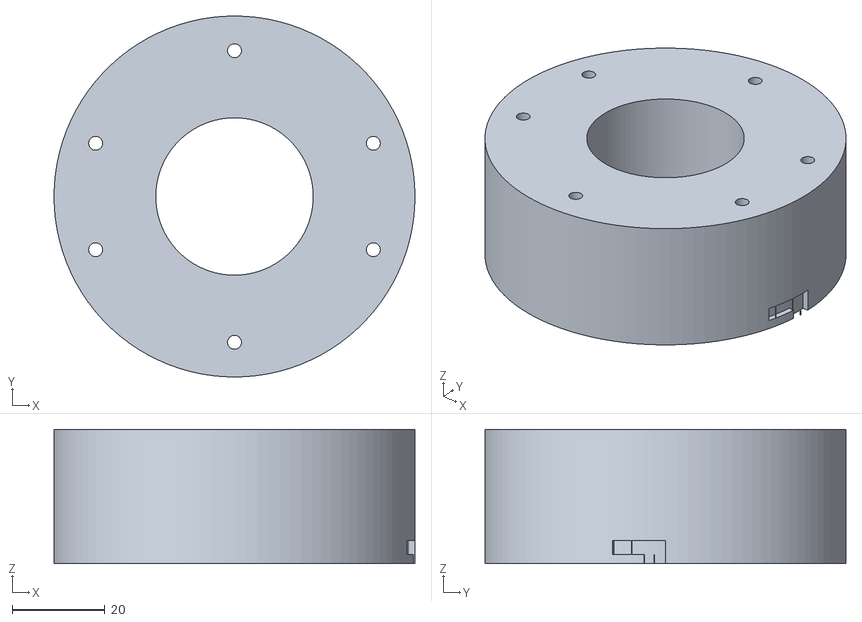
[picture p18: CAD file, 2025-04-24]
3Dmodels/STLs/led_ring_enclosure.stl
78.0 x 78.0 x 29.0

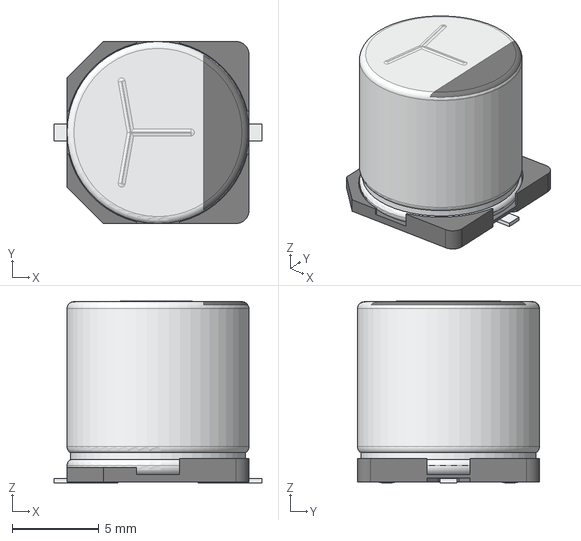
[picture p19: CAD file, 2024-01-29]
hardware/FOdriver_V2.0/ALTIUM_EMBEDDED_MODELS/CAPAE-D10.0x10.2.stp
12.0 x 10.5 x 10.5 mm

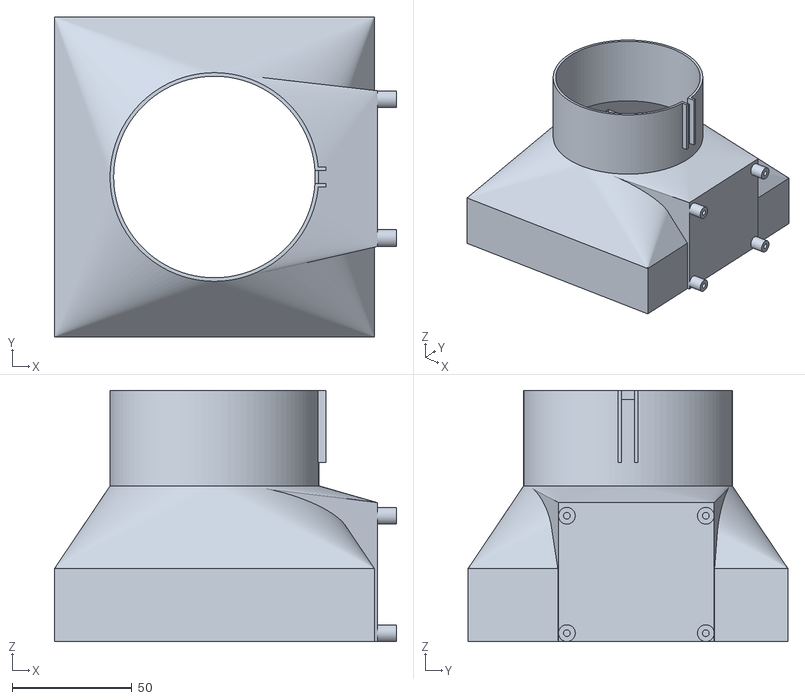
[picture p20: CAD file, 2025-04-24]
3Dmodels/STLs/cone_hull_short.stl
142.8 x 133.5 x 104.8

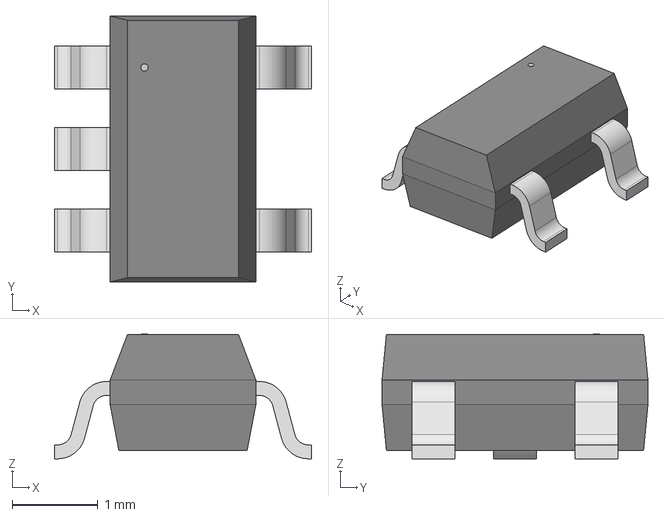
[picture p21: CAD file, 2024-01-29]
hardware/FOdriver_V2.0/ALTIUM_EMBEDDED_MODELS/SOT25.step
3.00 x 3.10 x 1.45 mm

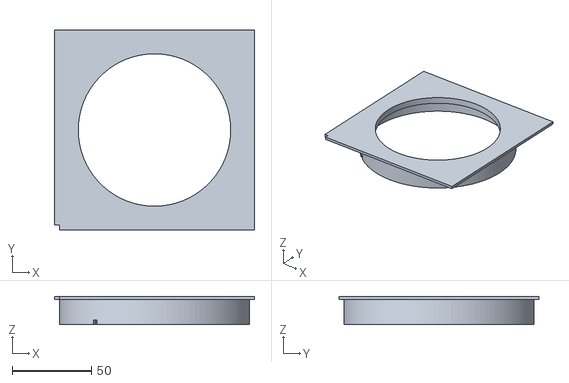
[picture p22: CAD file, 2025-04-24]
3Dmodels/STLs/diffuser_holder.stl
126.0 x 126.0 x 17.8

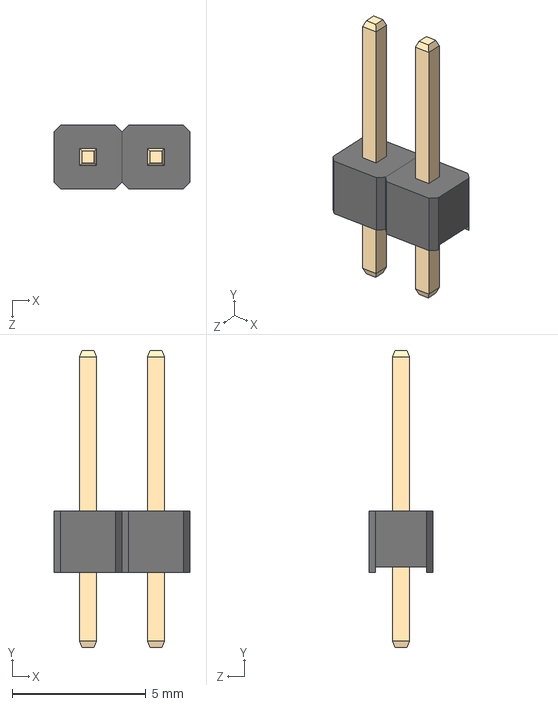
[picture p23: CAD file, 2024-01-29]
hardware/FOdriver_V2.0/ALTIUM_EMBEDDED_MODELS/2x_Male_Pin_2.54_mm.STEP
5.08 x 11.1 x 2.40 mm
1_Male_Pin_2.54_mm x 2

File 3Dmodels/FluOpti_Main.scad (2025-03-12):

/*
       This code is part of  a collaborative project between Lab Tecnologia Libre and IOWlabs 
    (c) Fernan Federici and Isaac Nuñez, 2022- Released under the CERN Open Hardware License   
*/

//include <picam_2_push_fit.scad>  
include <Flat_cam_holder.scad>  

//-------important parameters if you wish to change the petri dish size and the base dimensions below for customization

corr=0.2;// used to create extra fitting space for printing imperfections
petri_h=15;// petri dish height
petri_lid_d=92.4 + corr*3; //petri dish diameter, corr is added for extra space (e.g. parafilm)
LED_shield=40;//distance from illuminating hole to border used to hide the LEDs from the camera field of view

//-----------------secondary -parameters less likely to be changed

screw_d=21;//distance between screw holes in RPI camera holder
screw_r=2/2;//screw radius
screw_hold_r=2;
sensor_h=2; //space for sensor
sensor_x=8.5;//RPI camera sensor dim
wall_M12=1.5;
base_xy=16;
base_h=6;
M12_r=12/2;//radius of M12 lens
mount_h = 12;
wall=0.75;
holder_x=54;//acrylic bed width to fit into holder
holder_y=54;//acrylic bed thickness to fit into holder, normally 3mm acrylic
holder_z=3;//acrylic bed thickness to fit into holder, normally 3mm acrylic
h_ring= petri_h*2;//petri dish-holding ring 
light_box_h=50;
elastic_holder_dist=petri_lid_d+5;//petri_lid_d-8;// diameter of the illuminating hole, with a 4mm notch to hold the petri dish. It has to be smaller than petri_lid_d (Parkinson 2007 uses 82mm).


notch_y=11;
elastic_holder_xy=10;
elastic_holder_z=10;
M12_h=10;

PCB_optoLED_r=84/2;//how big is the ring from screw to screw
PCB_optoLED_r_ext=69/2;//external radius
PCB_optoLED_r_inte=41/2; //internal radius
PCB_LED_x=125;//155;// placa del FluOpti es de 15.5x11cm  y los agujeros estan a 3mm delos bordes en los dos ejes//
PCB_LED_y=81;//111;
diag=190; //diagonal of blue LED PCB (155 x 111)
cone_r=petri_lid_d/2*1.5;//bottom radius of cone
echo("cone r is", cone_r);

view_open_d=petri_lid_d-wall*4;
base_d=diag+wall*6;//diameter of printed light house cylinder
cone_r2=base_xy*2;//top radius
focus_h=40;
h_cam=90-h_ring;//height to camera 
inner_r=petri_lid_d*1.2/2;
velvet_background_ring_h=28;
LED_base_h=9;
LED_ring_ext_d=base_d-wall*3;
LED_ring_int_d=LED_ring_ext_d-10;
velvet_background_ring_d=LED_ring_int_d-wall*3;
velvet_background_ring_stage_r=velvet_background_ring_d/2-10;
inner_h=petri_h/2;
focus_r=cone_r2;
M13_neg_d=2.8;

wire_clearance_w=wall*7;
wire_clearance_x=wall*6;
wire_riel_h=focus_h*0.75;

raspi_z = 10;
raspi_board = [85, 58, 19]; // 3B model is 82*56*19.5mm and 4B is 88*58*19.5mm

//h = raspi_z + raspi_board[2] + 5;

echo(raspi_board[1]);

ITO_dim=100;
$fn=100;
    RG_ring_r=70/2;
    cone_r3=RG_ring_r+wall*8;
    
///////////////////////////
//// user defined values //
///////////////////////////
//r_inte = 48; // internal radius
//ri_thick = 1; // structure internal thickness
//re_thick_u = 3; // structure external thickness
//re_thick_d = 1; // structure external thickness
//z_thick = 2; // z structure thickness
//paper_space = 0.5; // space to fit the paper
//h_int = 3; // internal height where to fit paper
//

// for the arms
arm_z = 15; // arm z lenght
arm_tick = 3; // arm thickness

arm_hbt = 2.5; // hole borders thickness
ra_screw = 1.5; // ringholder-arms screw rad
s_arm_screw = 1.5; // arms screw hole separation from scafold.


plate_center= 66; //distance from the enclosure wall to the center of the plate.


// LED ring parameters

r_ext = 70/2; // external radius
r_int = 40/2; // internal radius
ring_h = 1.5; // PCB height
r_sh = 1.5; // screw holes radius
x_shd = 60; // screw holes x distance
y_shd = 23; // screw holes y distance
LED_z = 8; // LEDs height

CCFB = plate_center - holder_y; // Camera Center From Border

//// external square support
//sq_x = 126;
//sq_y = 126;
//sq_thick = 2;

//c_hole_w = 3;  //cable hole wide
//c_hole_h = 3; //cable hole height
//b_dist = 6; // base support border distance, defined on the central axis
//b_thick = 2;
//base_h_sq = 15.8-sq_thick+z_thick;  // related to diffuser h

//x_displace = 3;  // hole displcement arround x axis

// for the ring enclosure
re_zt = 2; // ring enclosure z thickness
re_rt = 2; // ring enclosure r thickness
re_scw = 1.5; //screw supports thickness
re_rfe = 2; // ring enclosure r free space  (between the PCB and external enclosure in r axis)
re_rfei = 1; // ring enclosure r free space internal hole (between the PCB and internal enclosure in r axis)

re_fh = 18.5; // front height. This is the LED height after having soldered them
re_dh = 3; // difussor separation from LEDs 
re_bh = 4; // back heigh. Left some air space equivalent to the screw support lenght
chs_x = 3; // cable hole space in x axis
chs_z = 3; // cable hole space in z axis. This value is added over the clamp height

re_cd = 1; // clamp deep
re_cw = 4; // clamp wide
re_ch = 2; // clamp height
re_cdh = re_cd + 0.3; // clamp deep hole, 0.3 looseness 
re_cw1 = re_cw + 0.5; // clamp wide 1st section, 1 looseness
re_cw2 = 2.5*re_cw1; // clamp wide 2nd section
re_ch1 = 2; // clamp height 1st section
re_ch2 = re_ch + 1; // clamp height 2nd section, 1 looseness

hre = re_dh + re_fh + ring_h +re_bh + re_zt ; // ring enclosure heigh
rre = r_ext + re_rfe + re_rt;//ring enclosure radius
echo("rre is", rre);
 lrd_r = rre+re_rt+0.3;
echo("lrd_r is", lrd_r);
rrei = r_int-re_rfei;// ring enclosure internal radius



//// computed values
//r_ext_up = r_int+re_thick_u+ri_thick+paper_space;
//r_ext_down = r_int+re_thick_d+ri_thick+paper_space;
//h_total = h_int+z_thick;


//------------Uncomment items below to render each piece--------------------------




//translate([ 0.00, 0.00, 150.00 ]) rotate([0,0,40]) cone_window_lid();  


translate([0,0,-10]) top_part(); 

//translate([ 0.00, 0.00, -150.00 ]) cone_hull_short();//usar este

//translate([ 0.00, 0.00, 55.00 ]) diffuser_holder(true);

//translate([ 0.00, 0.00, 0.00 ]) plate_holder();// .

//lighting_base_squared();

//rotate([0,180,0])led_ring_enclosure();




//------------------------------------------------------------------------------------------------------

//led_ring_enclosure();
module led_ring_enclosure(){
    // to create the PCB ring enclosure
        
    difference(){
        union(){
            // base cylinder
            difference(){
            color("red")cylinder($fn = 100, h=hre, r=rre, center=true);
            translate([0,0,re_zt/2+wall])
            color("white") cylinder($fn = 100, h=hre-re_zt+wall, r=rre-re_rt, center=true);
            }
            
            // internal cylinder
            cylinder($fn = 100, h=hre, r=rrei, center=true);
            
            // screw supports for LED ring
           color("blue") for (x =[x_shd/2,-x_shd/2]){
                for (y =[y_shd/2,-y_shd/2]){ 
                    translate([x,y,(re_bh-hre)/2+re_zt])
                    cylinder($fn = 100, h=re_bh, r=rh_screw + r_sh, center=true);
                }
            }
        }
            // internal hole
            cylinder($fn = 100, h=hre+wall, r=rrei-re_rt, center=true);
            
            // screw holes for LED ring
            for (x =[x_shd/2,-x_shd/2]){
                for (y =[y_shd/2,-y_shd/2]){ 
                    translate([x,y,(re_bh-hre+re_zt)/2])
                     color("red") cylinder($fn = 100, h=re_bh+re_zt, r=r_sh, center=true);
                }
            }
            
            //cable hole
            chsz_final = chs_z + re_ch1 + re_ch2;
            translate([0,rre-0.5*re_rt,(hre-chsz_final)/2])
            cube([chs_x,2*re_rt,chsz_final], center = true);
            
            //arms hole to hold the module to the ceiling of the device
            xash = scafold_x/2 +ra_screw;
            
                 for (x =[xash,-xash]){
                 translate([0,x,(re_zt-hre)/2])
                color("yellow") cylinder($fn = 100, h=re_zt*2, r=ra_screw, center=true);
                }
                
                
//            for (x =[xash,-xash]){
//                translate([x,0,(re_zt-hre)/2])
//                cylinder($fn = 100, h=re_zt*2, r=ra_screw, center=true);
//                }
            
            // Clamp
            for (rc =[rre-re_cdh,-(rre)]){
                
                // enter track
                c_angle1 = (re_cw1/(rre - re_cdh))*360/(2*PI);
                translate([0,0,hre/2-re_ch1])
                rotate_extrude(angle = c_angle1,convexity = 5, $fn = 500)
                translate([rc,0,0])
                polygon( points=[[0,0],[0,re_ch1],[re_cdh,re_ch1],[re_cdh,0]] );
                
                // horizontal track
                c_angle2 = (re_cw2/(rre - re_cdh))*360/(2*PI);
                translate([0,0,hre/2-(re_ch1+re_ch2)])
                rotate_extrude(angle = c_angle2,convexity = 5, $fn = 500)
                translate([rc,0,0])
                polygon( points=[[0,0],[0,re_ch2],[re_cdh,re_ch2],[re_cdh,0]] );
            }

    }
    
}
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

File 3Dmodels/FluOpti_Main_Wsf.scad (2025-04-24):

/*
    FluOpti - Fluorescence Microscopy Optimization Device
    Part of a collaborative project between Lab Tecnologia Libre and IOWlabs
    (c) Fernan Federici and Isaac Nuñez, 2022
    Released under the CERN Open Hardware License
*/

include <Flat_cam_holder.scad>

// Primary Configuration Parameters
// ------------------------------

// Correction factor for 3D printing tolerances
corr = 0.2;  // mm, extra fitting space for printing imperfections

// Petri Dish Parameters
petri_h = 15;        // mm, petri dish height
petri_lid_d = 92.4 + corr*3;  // mm, petri dish diameter with tolerance

// LED Configuration
LED_shield = 40;     // mm, distance from illuminating hole to border (prevents LED light bleeding)

// Secondary Configuration Parameters
// -------------------------------

// Camera Mount Parameters
screw_d = 21;        // mm, distance between screw holes in RPI camera holder
screw_r = 1;         // mm, screw radius (2/2 simplified)
screw_hold_r = 2;    // mm, screw holder radius
sensor_h = 2;        // mm, space for sensor
sensor_x = 8.5;      // mm, RPI camera sensor dimension

// Base Structure Parameters
wall_M12 = 1.5;      // mm, wall thickness for M12 lens mount
base_xy = 16;        // mm, base width and length
base_h = 6;          // mm, base height
M12_r = 6;           // mm, radius of M12 lens (12/2 simplified)
mount_h = 12;        // mm, mount height
wall = 0.75;         // mm, standard wall thickness

// Base Holder Parameters
base_holder_thickness = 8;     // mm, thickness of the holder base
base_holder_margin = 15;       // mm, extra margin around the base
base_holder_height = 25;       // mm, height of the holder walls
mount_screw_d = 4;             // mm, diameter of mounting screws
mount_screw_head_d = 7;        // mm, diameter of screw head
mount_screw_head_h = 3;        // mm, height of screw head

// Ventilation Parameters
vent_hole_d = 8;               // mm, diameter of ventilation holes
vent_hole_spacing = 15;        // mm, spacing between ventilation holes
foot_height = 10;              // mm, height of the feet
foot_d = 10;                   // mm, diameter of feet base
foot_top_d = 12;               // mm, diameter of feet top

// Holder Parameters
holder_x = 54;       // mm, acrylic bed width
holder_y = 54;       // mm, acrylic bed length
holder_z = 3;        // mm, acrylic bed thickness (3mm standard)

// Ring and Box Parameters
h_ring = petri_h * 2; // mm, petri dish-holding ring height
light_box_h = 50;    // mm, light box height
elastic_holder_dist = petri_lid_d + 5;  // mm, illuminating hole diameter with notch

// Holder and Notch Parameters
notch_y = 11;            // mm, notch height
elastic_holder_xy = 10;  // mm, elastic holder width and length
elastic_holder_z = 10;   // mm, elastic holder height
M12_h = 10;              // mm, M12 lens mount height

// PCB and LED Parameters
PCB_optoLED_r = 42;     // mm, ring radius from screw to screw (84/2)
PCB_optoLED_r_ext = 34.5;  // mm, external radius (69/2)
PCB_optoLED_r_inte = 20.5; // mm, internal radius (41/2)
PCB_LED_x = 125;        // mm, FluOpti PCB width
PCB_LED_y = 81;         // mm, FluOpti PCB length
diag = 190;             // mm, diagonal of blue LED PCB

// Cone and Base Parameters
cone_r = petri_lid_d/2 * 1.5;  // mm, bottom radius of cone
view_open_d = petri_lid_d - wall*4;  // mm, viewing opening diameter
base_d = diag + wall*6;  // mm, light house cylinder diameter
cone_r2 = base_xy * 2;   // mm, top radius
focus_h = 40;            // mm, focus height
h_cam = 90 - h_ring;     // mm, height to camera

// Ring Parameters
inner_r = petri_lid_d * 1.2/2;  // mm, inner radius
velvet_background_ring_h = 28;   // mm, background ring height
LED_base_h = 9;          // mm, LED base height
LED_ring_ext_d = base_d - wall*3;  // mm, LED ring external diameter
LED_ring_int_d = LED_ring_ext_d - 10;  // mm, LED ring internal diameter
velvet_background_ring_d = LED_ring_int_d - wall*3;  // mm, background ring diameter
velvet_background_ring_stage_r = velvet_background_ring_d/2 - 10;  // mm, stage radius
inner_h = petri_h/2;     // mm, inner height
focus_r = cone_r2;       // mm, focus radius
M13_neg_d = 2.8;         // mm, M13 negative diameter

// Wire and Clearance Parameters
wire_clearance_w = wall * 7;  // mm, wire clearance width
wire_clearance_x = wall * 6;  // mm, wire clearance length
wire_riel_h = focus_h * 0.75; // mm, wire rail height

// Raspberry Pi Parameters
raspi_z = 10;  // mm, Raspberry Pi Z offset
raspi_board = [85, 58, 19];  // mm, RPi board dimensions [width, length, height]

// Rendering Quality
$fn = 100;  // facet number for curved surfaces

// Additional Parameters
ITO_dim = 100;      // mm, ITO glass dimension
RG_ring_r = 35;     // mm, ring radius (70/2)
cone_r3 = RG_ring_r + wall * 8;  // mm, cone radius

// Arm Parameters
arm_z = 15;          // mm, arm z length
arm_tick = 3;        // mm, arm thickness
arm_hbt = 2.5;       // mm, hole borders thickness
ra_screw = 1.5;      // mm, ringholder-arms screw radius
s_arm_screw = 1.5;   // mm, arms screw hole separation from scaffold

// Plate Parameters
plate_center = 66;    // mm, distance from enclosure wall to plate center

// LED Ring Parameters
r_ext = 35;          // mm, external radius (70/2)
r_int = 20;          // mm, internal radius (40/2)
ring_h = 1.5;        // mm, PCB height
r_sh = 1.5;          // mm, screw holes radius
x_shd = 60;          // mm, screw holes x distance
y_shd = 23;          // mm, screw holes y distance
LED_z = 8;           // mm, LEDs height

// Camera Position
CCFB = plate_center - holder_y;  // mm, Camera Center From Border

//// external square support
//sq_x = 126;
//sq_y = 126;
//sq_thick = 2;

//c_hole_w = 3;  //cable hole wide
//c_hole_h = 3; //cable hole height
//b_dist = 6; // base support border distance, defined on the central axis
//b_thick = 2;
//base_h_sq = 15.8-sq_thick+z_thick;  // related to diffuser h

//x_displace = 3;  // hole displcement arround x axis

// for the ring enclosure
re_zt = 2; // ring enclosure z thickness
re_rt = 2; // ring enclosure r thickness
re_scw = 1.5; //screw supports thickness
re_rfe = 2; // ring enclosure r free space  (between the PCB and external enclosure in r axis)
re_rfei = 1; // ring enclosure r free space internal hole (between the PCB and internal enclosure in r axis)

re_fh = 18.5; // front height. This is the LED height after having soldered them
re_dh = 3; // difussor separation from LEDs 
re_bh = 4; // back heigh. Left some air space equivalent to the screw support lenght
chs_x = 3; // cable hole space in x axis
chs_z = 3; // cable hole space in z axis. This value is added over the clamp height

re_cd = 1; // clamp deep
re_cw = 4; // clamp wide
re_ch = 2; // clamp height
re_cdh = re_cd + 0.3; // clamp deep hole, 0.3 looseness 
re_cw1 = re_cw + 0.5; // clamp wide 1st section, 1 looseness
re_cw2 = 2.5*re_cw1; // clamp wide 2nd section
re_ch1 = 2; // clamp height 1st section
re_ch2 = re_ch + 1; // clamp height 2nd section, 1 looseness

hre = re_dh + re_fh + ring_h +re_bh + re_zt ; // ring enclosure heigh
rre = r_ext + re_rfe + re_rt;//ring enclosure radius
echo("rre is", rre);
 lrd_r = rre+re_rt+0.3;
echo("lrd_r is", lrd_r);
rrei = r_int-re_rfei;// ring enclosure internal radius

 int_top_cyl_r=lrd_r+wall;
roof_thick_h=10; //to screw holder and camera in


//// computed values
//r_ext_up = r_int+re_thick_u+ri_thick+paper_space;
//r_ext_down = r_int+re_thick_d+ri_thick+paper_space;
//h_total = h_int+z_thick;


//------------Uncomment items below to render each piece--------------------------




translate([0,0,200]) top_part(); 

//translate([ 0.00, 0.00, 70.00 ]) cone_hull_short();//usar este
//
//translate([ 0.00, 0.00, 170.00 ]) rotate([0,180,0])led_ring_enclosure();
//
//translate([ 0.00, 0.00, 55.00 ]) diffuser_holder(true);
//
//translate([ 0.00, 0.00, 0.00 ]) plate_holder();// .
//
//translate([ 0.00, 0.00, -60.00 ]) lighting_base_squared();

// Render the base holder
//translate([0, 0, -170]) base_holder();

// Render the lighting base (commented out for testing)
//translate([0, 0, base_holder_height]) lighting_base_squared();




//------------------------------------------------------------------------------------------------------
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

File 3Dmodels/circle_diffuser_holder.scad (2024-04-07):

/*
    Isaac Núñez 2020 (CC BY 4.0; https://creativecommons.org/licenses/by/4.0/) 
 
    This code generate the estructure for the 
    white ligth module of the Fluopi equipment.
 
*/


/////////////////////////
// user defined values //
/////////////////////////
r_int = 48; // internal radius
ri_thick = 1; // structure internal thickness
re_thick_u = 3; // structure external thickness
re_thick_d = 1; // structure external thickness
z_thick = 2; // z structure thickness
paper_space = 0.5; // space to fit the paper
h_int = 3; // internal height where to fit paper

// external square support
sq_x = 126;
sq_y = 126;
sq_thick = 2;

c_hole_w = 3;  //cable hole wide
c_hole_h = 3; //cable hole height
b_dist = 6; // base support border distance, defined on the central axis
b_thick = 2;
base_h = 15.8-sq_thick+z_thick;  // related to diffuser h

x_displace = 3;  // hole displcement arround x axis


// computed values
r_ext_up = r_int+re_thick_u+ri_thick+paper_space;
r_ext_down = r_int+re_thick_d+ri_thick+paper_space;
h_total = h_int+z_thick;



module ring(H,re_up,re_down,ri){
    difference(){
    cylinder(h = H, r1 = re_down, r2= re_up, center = true,$fn = 100);
        cylinder(h = H, r = ri, center = true,$fn = 100);
    }
    
}


module square_structure(){
    
    //base_x = sq_x - b_dist_x;
    //base_y = sq_y - b_dist_y;
    r_b = (sq_x-b_dist)/2;
    ri_b = r_b - b_thick;
    
    translate([0,0,-sq_thick/2])
    difference(){
        translate([x_displace,0,0])
    cube([sq_x,sq_y,sq_thick], center = true);

        translate([0,0,0])
            cylinder(h = sq_thick, r = r_ext_up, center = true,$fn = 100);translate([x_displace+(c_hole_w-sq_x)/2,(c_hole_w-sq_y)/2,0])
            cube([c_hole_w,c_hole_h,sq_thick], center = true);

    }
    

    translate([0,0,-base_h/2-sq_thick])
    difference(){
    ring(base_h,r_b,r_b,ri_b);
        //this part should be corrected...
        // it's not a general solution
    rotate(230)
   translate([r_b/2,0,-base_h/2])
    cube([r_b/2,c_hole_w,c_hole_w]);
    }

/*
        
    translate([0,0,-base_h/2-sq_thick])
    difference(){
    cube([base_x,base_y,base_h], center = true);
    cube([base_x-sq_thick,base_y-sq_thick,base_h], center = true);
        translate([(sq_thick-base_x)/2,c_hole_w-base_y/2,(c_hole_h-base_h)/2])
            cube([sq_thick,c_hole_w,c_hole_h], center = true);
    }
    
*/
    
    
}

module diffuser_holder(sq){
    
    re_space = r_ext_down-re_thick_d;
    ri_space = r_int+ri_thick;
    
        translate([0,0,-h_total/2])
    difference(){
    ring(h_total,r_ext_up,r_ext_down,r_int);
        translate([0,0,-z_thick])ring(h_total,re_space,re_space,ri_space);
    }
    
    if (sq == true){
    square_structure();
    }
    
    
    
}


/*
module cam_holder_base() {
    
    difference(){
    cube([scafold_x,scafold_y,scafold_z], center=true);
     translate([0,0,sca_trans])cube([holder_x,scafold_y*1.1,holder_z], center=true);
     translate([0,sca_deep/2,0])cube([scafold_x - 2*sca_arms_width,scafold_y - sca_deep,scafold_z], center=true);
     translate([holder_x/2-sca_arms_space/2,sca_deep/2,scafold_z/2])cube([sca_arms_space,scafold_y - sca_deep,scafold_z], center=true);
     translate([-holder_x/2+sca_arms_space/2,sca_deep/2,scafold_z/2])cube([sca_arms_space,scafold_y - sca_deep,scafold_z], center=true);
        
        }
 
}

module ring_holder(){
    
     translate([0,0,ring_spacer_z])difference(){
  translate([(scafold_x+ring_hold_x)/2,(waveshare_cam_y-scafold_y)/2+back_thick,(scafold_z-ring_hold_z)/2])cube([ring_hold_x*1.1,ring_hold_y,ring_hold_z], center=true);
  translate([(scafold_x+ring_hold_x)/2+screw_x_space,(waveshare_cam_y-scafold_y)/2+back_thick,(scafold_z-ring_hold_z)/2])cube([ring_hold_x*1.1,screw_d,ring_hold_z], center=true);

  }
  translate([(scafold_x-sca_thick_side)/2,(waveshare_cam_y-scafold_y)/2+back_thick,scafold_z/2 +ring_spacer_z/2])cube([sca_thick_side,ring_hold_y,ring_spacer_z], center=true);    
    }
module camera_mount(camera){

    if(camera == waveshare){
            cam_x = waveshare_cam_x;
            cam_y = waveshare_cam_y;
            cam_z = waveshare_cam_z;
    
    support_z = cam_z+bottom_thick;
    support_y = hold_y + back_thick;
    translate([0,-scafold_y/2 + support_y/2,scafold_z/2+support_z/2])difference(){cube([cam_x+2*side_thick,support_y,support_z], center=true);
        translate([0,back_thick/2,-bottom_thick/2])cube([cam_x,hold_y,cam_z], center=true);
        translate([0,0,0])cube([cam_x - 2*hold_x,support_y,support_z], center=true);
    }
    }
}

side_thick = 2; //side support thickness
bottom_thick = 1; // bottom support thickness
back_thick
waveshare_cam_x=32.2;
waveshare_cam_y=1.5; //thickness
waveshare_cam_z=32.2;
hold_x = 4.8;    // space between border and cable conector
hold_y = 4.2;  // space between border and resistor
*/

diffuser_holder(true);
//square_structure();

/*
            rotate_extrude(angle = 120, convexity = 2){
    translate([10, 0, 0])
    square([b_thick,c_hole_h],center);
            }
*/
/*
true: to include the external square support, 
false: to just create the ring
*/

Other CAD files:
hardware/FOdriver_V2.0/ALTIUM_EMBEDDED_MODELS/ASPI-8040S.STEP
hardware/FOdriver_V2.0/ALTIUM_EMBEDDED_MODELS/PLS-3.step
hardware/FOdriver_V2.0/ALTIUM_EMBEDDED_MODELS/IND_CDRH127LDNP-470MC_SUM.step
hardware/FOdriver_V2.0/ALTIUM_EMBEDDED_MODELS/DGK0008A.stp
3Dmodels/Flat_cam_holder.scad
3Dmodels/picam_2_push_fit.scad
3Dmodels/utilities.scad
hardware/FOdriver_V2.0/ALTIUM_EMBEDDED_MODELS/015477608.stp
hardware/FOdriver_V2.0/ALTIUM_EMBEDDED_MODELS/430450212.stp
hardware/FOdriver_V2.0/ALTIUM_EMBEDDED_MODELS/69730.stp
hardware/FOdriver_V2.0/ALTIUM_EMBEDDED_MODELS/705430002.stp
hardware/FOdriver_V2.0/ALTIUM_EMBEDDED_MODELS/705430036.stp
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

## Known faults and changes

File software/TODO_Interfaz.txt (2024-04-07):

**TODO's pendientes de la interfaz **

Actualmente la interfaz es funcional considerando n° maximo de bloques (6). De esta forma, se pueden setear hasta 6 bloques con sus tiempos respectivos, e intensidad de led verde y rojo en cada bloque. Además, se implemento una funcionalidad para setear infinitos patrones de fotos que al apretar el boton "Guardar" se guardan en un diccionario que se entrega a la MainWindow (gui_test_v3). En la configuracion de seteo de patrones se puede ver el preview de la foto a tomar y configurar distintos parametros de la cámara.

TODO's:

1.- Hacer la logica que haga que se tomen las fotos segun los tiempos (segun frecuencia seteada) y parametros seteados en el diccionario de patrones. Probablemente haya que usar threads para tomar fotos para que la interfaz no se quede pegada ("No responde").

2.- Hacer que los bloques posibles sean infinitos (Se puede seguir el ejemplo usado para los patrones). Sin embargo, esto tiene el problema de que habría que hacer una logica para eliminar algún bloque que haya quedado mal configurado. Lo que puede ser engorroso. Al mismo tiempo, si se hace eso, se debería mostrar en la interfaz los bloques actuales que estan configurados, y los patrones actuales que estan configurados (Había dejado un GroupBox llamado "Patron de Fotos Seteado" puesto para poner esto, pero hay que ver si eso queda bien).

3.- Implementar que al tomar las fotos, se guarde la metadata de estas. (Creo que en las funciones implementadas por Isaac ya se hace esto, pero habría que integrarlo)

4.- Agregar 2da temperatura de control y conectar logica de control de temperatura a la interfaz. Actualmente la temperatura seteada por interfaz no se encuentra conectada a ningúna parte del backend (basicamente no toque nada del control de temperatura).

5.- Exportar e importar datos. Editar y elimar bloques o patrones.

6.- Cambiar la duración de los bloques de segundos a horas (Esto esta comentado en el metodo run de ExperimentoThread).

7.- Hacer que al agregar un nuevo bloque, se pongan por defecto los parametros del bloque anterior.

8.- Agregar boton de "Restablecer por defecto" en la ventana de configuracion de patron de fotos. Esto por si el usuario movió mucho los parametros, sea más facil volver a los que estaban por defecto.

Flujo programa (considerando estado actual, sin los TODO's propuestos):

El flujo ideal del programa sería ir a la tab de "RUN", luego elegir el numero de bloques que se quieren configurar y apretar "configurar bloques". Esto llamara a una ventana emergente que permitirá elegir los parametros de tiempo_exp, intensidad de led verde y rojo, así como temperatura de control. Una vez seleccionados los parametros, se aprieta "Guardar", y con esto se cierra la ventana emergente y se muestran los bloques escogidos en la interfaz.

Luego, se puede apretar el boton de configuración de foto para agregar una nueva configuración de patrón y seguir la logica anterior. 

Finalmente, al apretar el boton "run", comienza el experimento (se marca el tiempo actual y el total) y se prenden los leds con la intensidad seteada, durante el tiempo específicado.

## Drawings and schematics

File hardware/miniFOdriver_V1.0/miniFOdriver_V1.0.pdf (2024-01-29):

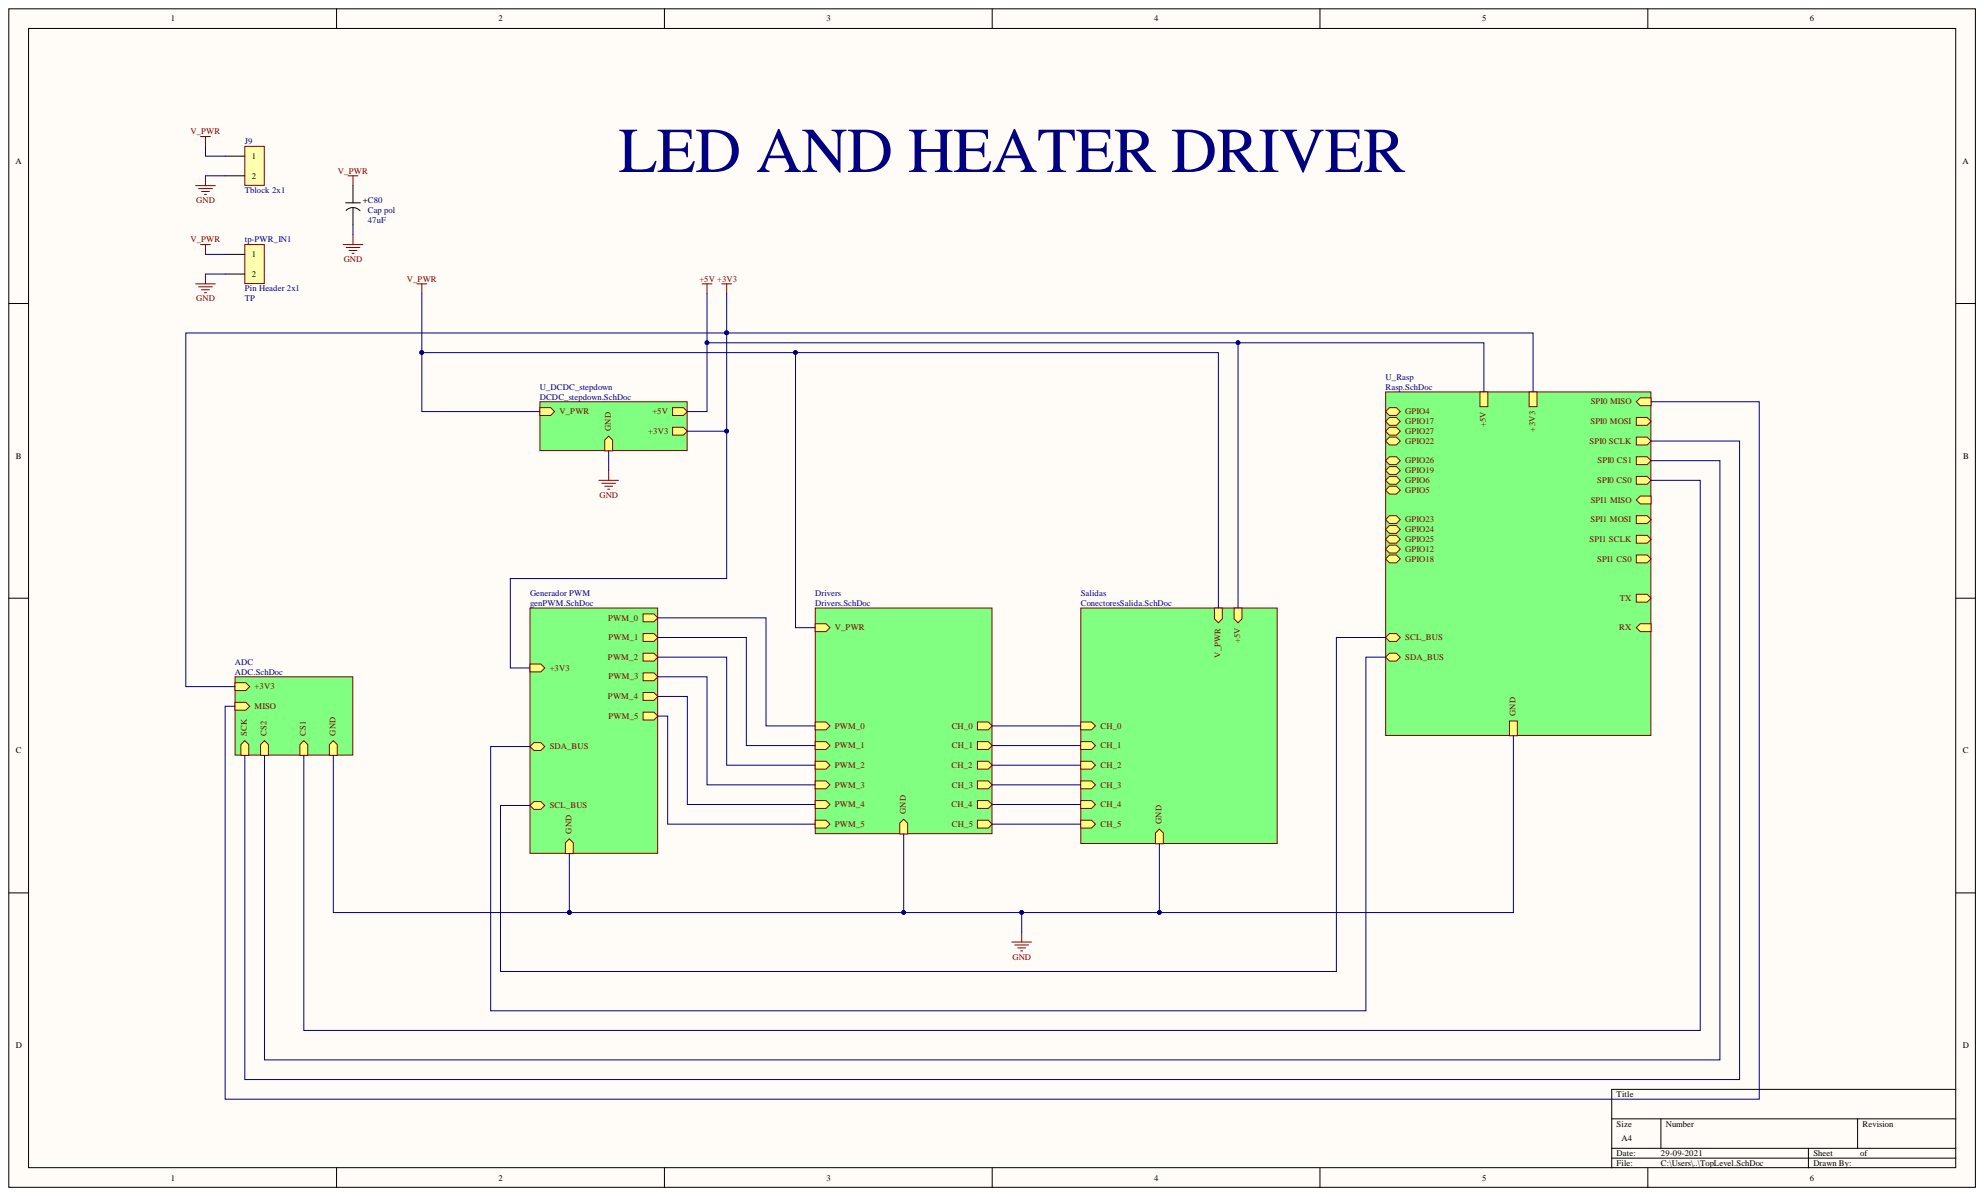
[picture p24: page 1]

LED AND HEATER DRIVER

U_Rasp Rasp.SchDoc

GPIO4 GPIO17 SPI0 MOSI GPIO27 GPIO22 SPI0 SCLK

GPIO26 SPI0 CS1
GPIO19 GPIO6 SPI0 CS0

GND | Drivers Salidas Drivers.SchDoc ConectoresSalida.SchDoc | GPIO5 SPI1 MISO GPIO23 SPI1 MOSI GPIO24 GPIO25 SPI1 SCLK GPIO12 GPIO18 SPI1 CS0 TX RX SCL_BUS SDA_BUS

PWM_0 PWM_1 PWM_2 +3V3 PWM_3 PWM_4 PWM_5 SDA_BUS | V_PWR PWM_0 CH_0 PWM_1 CH_1 PWM_2 CH_2 PWM_3 CH_3 PWM_4 CH_4 PWM_5 CH_5 | CH_0

+3V3 MISO

SCL_BUS

Size A4 | Number | Revision

Date: 29-09-2021 | Sheet of
File: C:\Users\..\TopLevel.SchDoc | Drawn By:

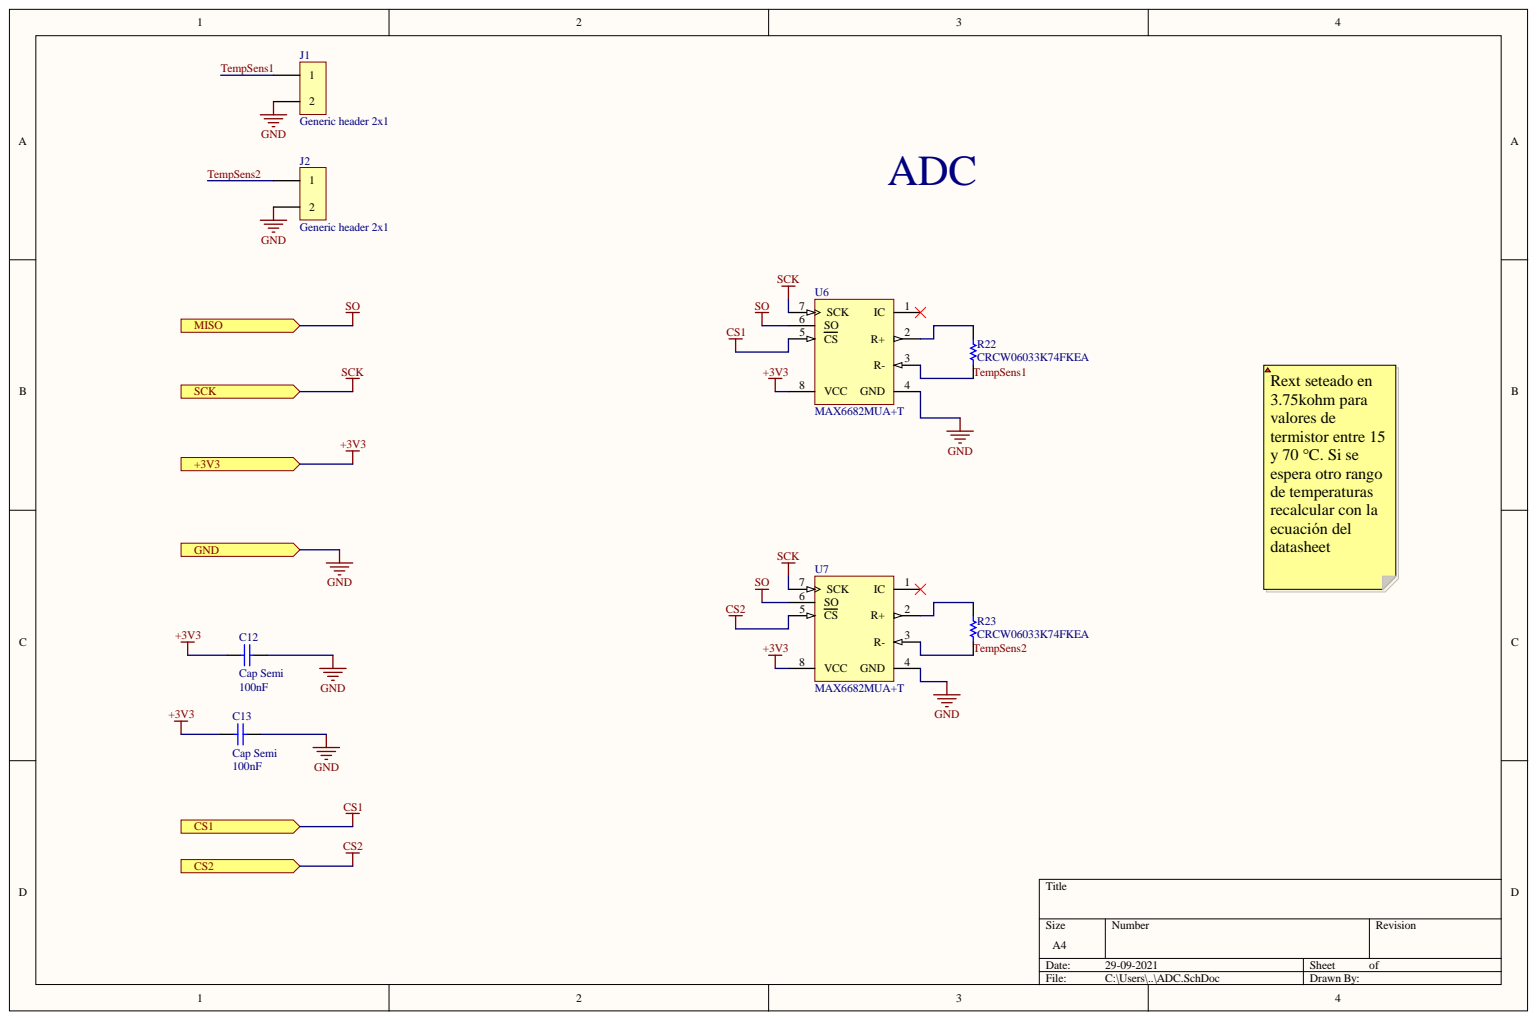
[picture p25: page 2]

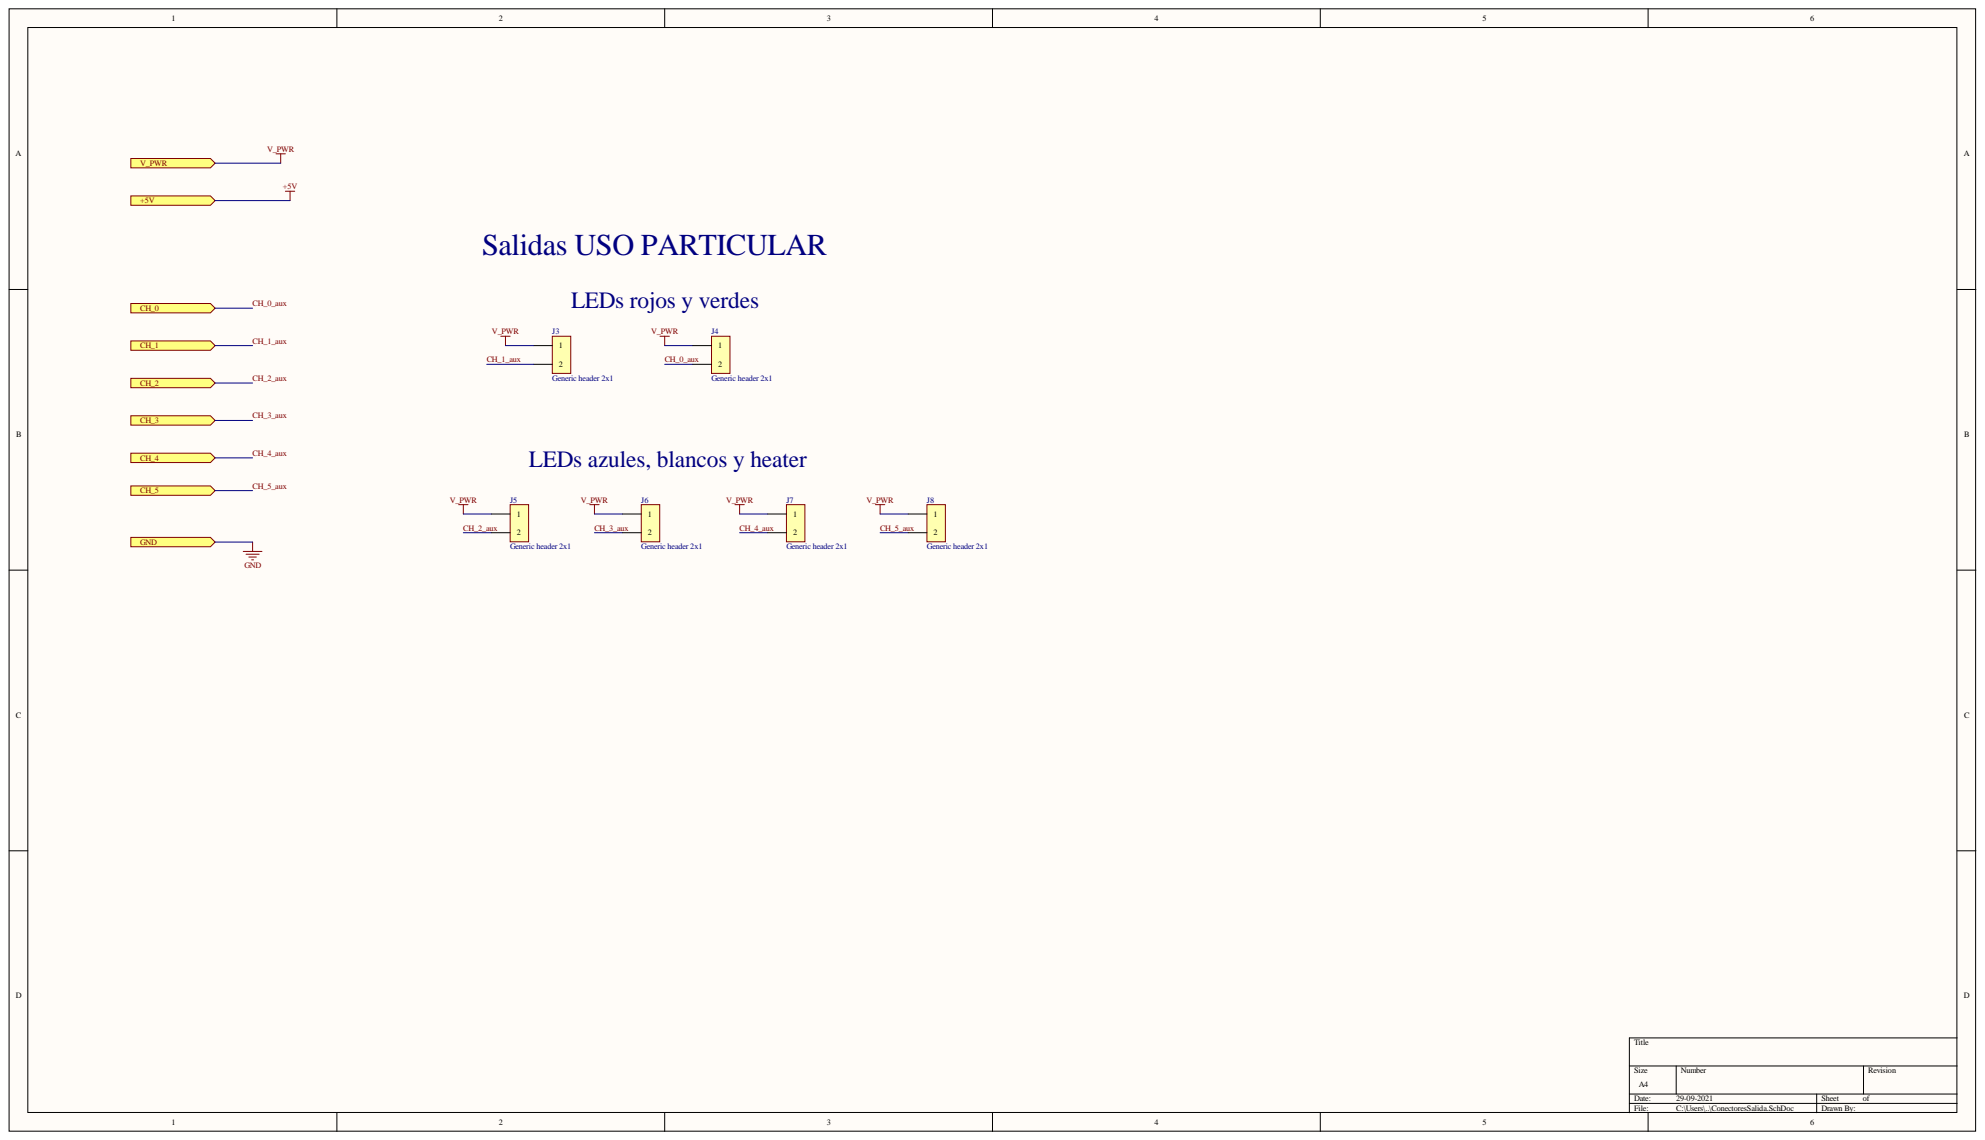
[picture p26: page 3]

LEDs azules, blancos y heater

Size A4 | Number | Revision

Date: 29-09-2021 | Sheet of
File: C:\Users\..\ConectoresSalida.SchDoc | Drawn By:

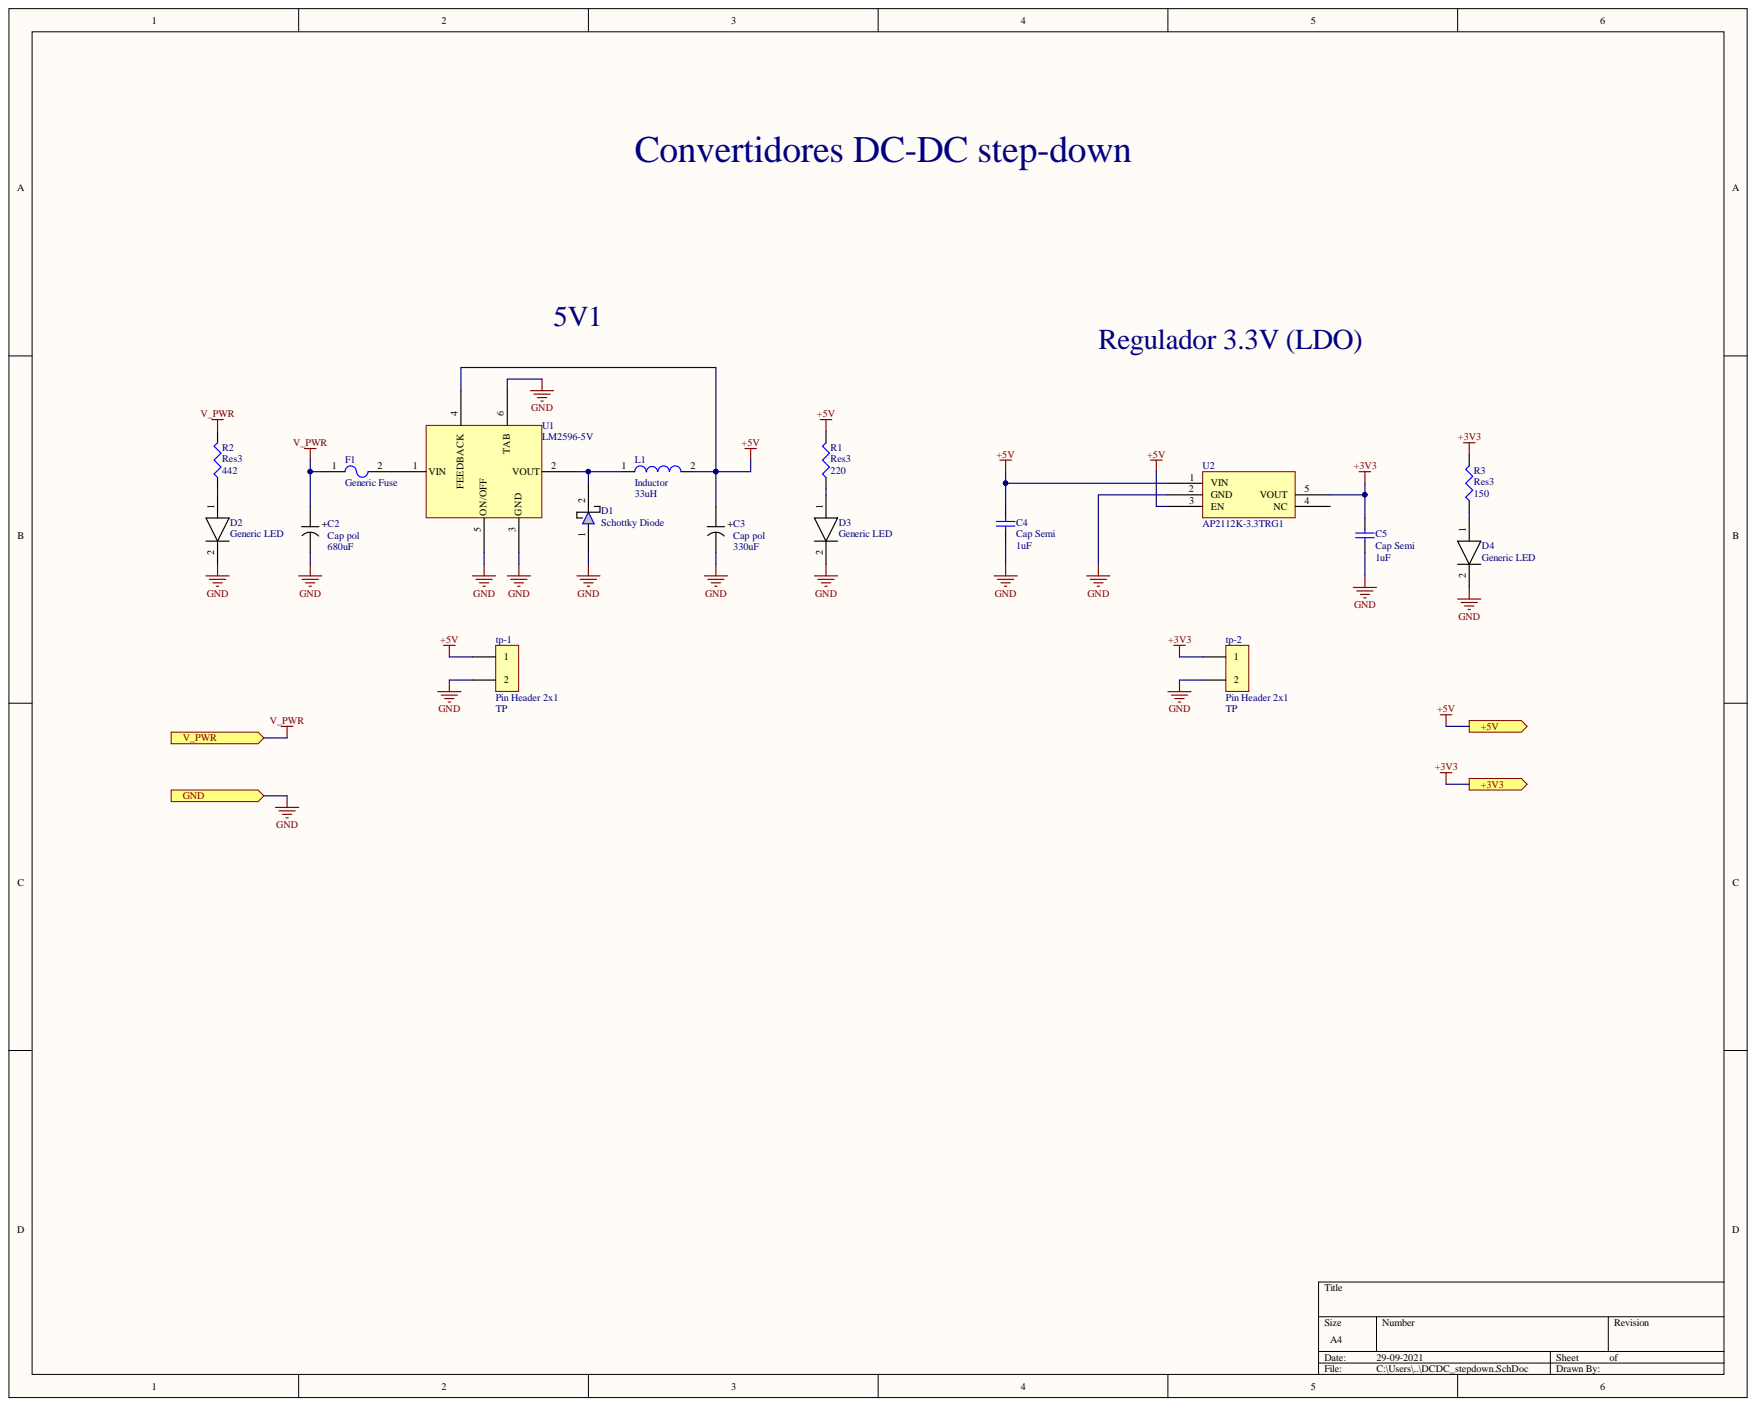
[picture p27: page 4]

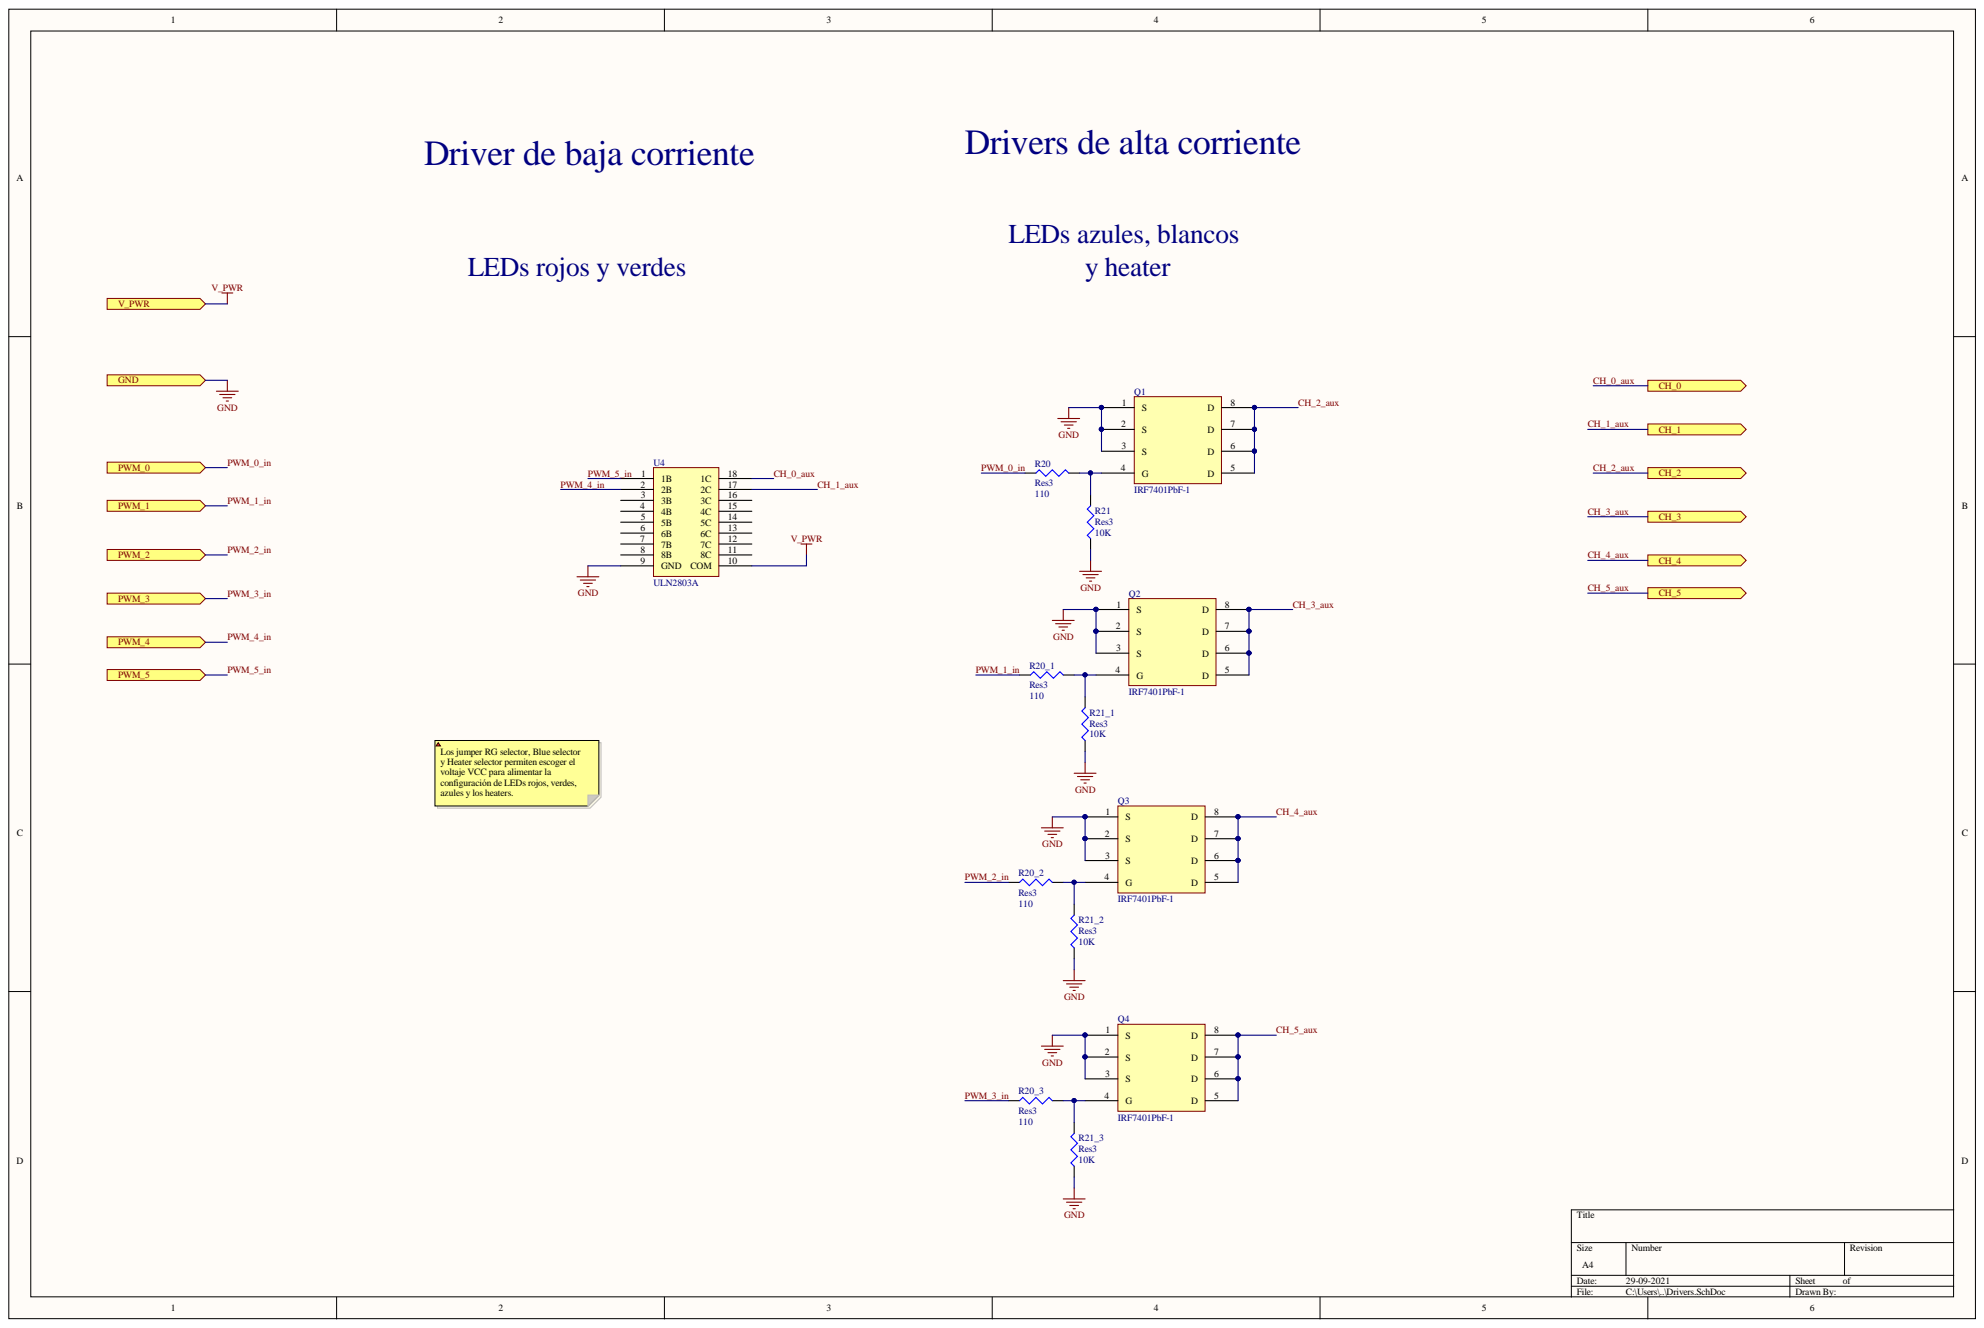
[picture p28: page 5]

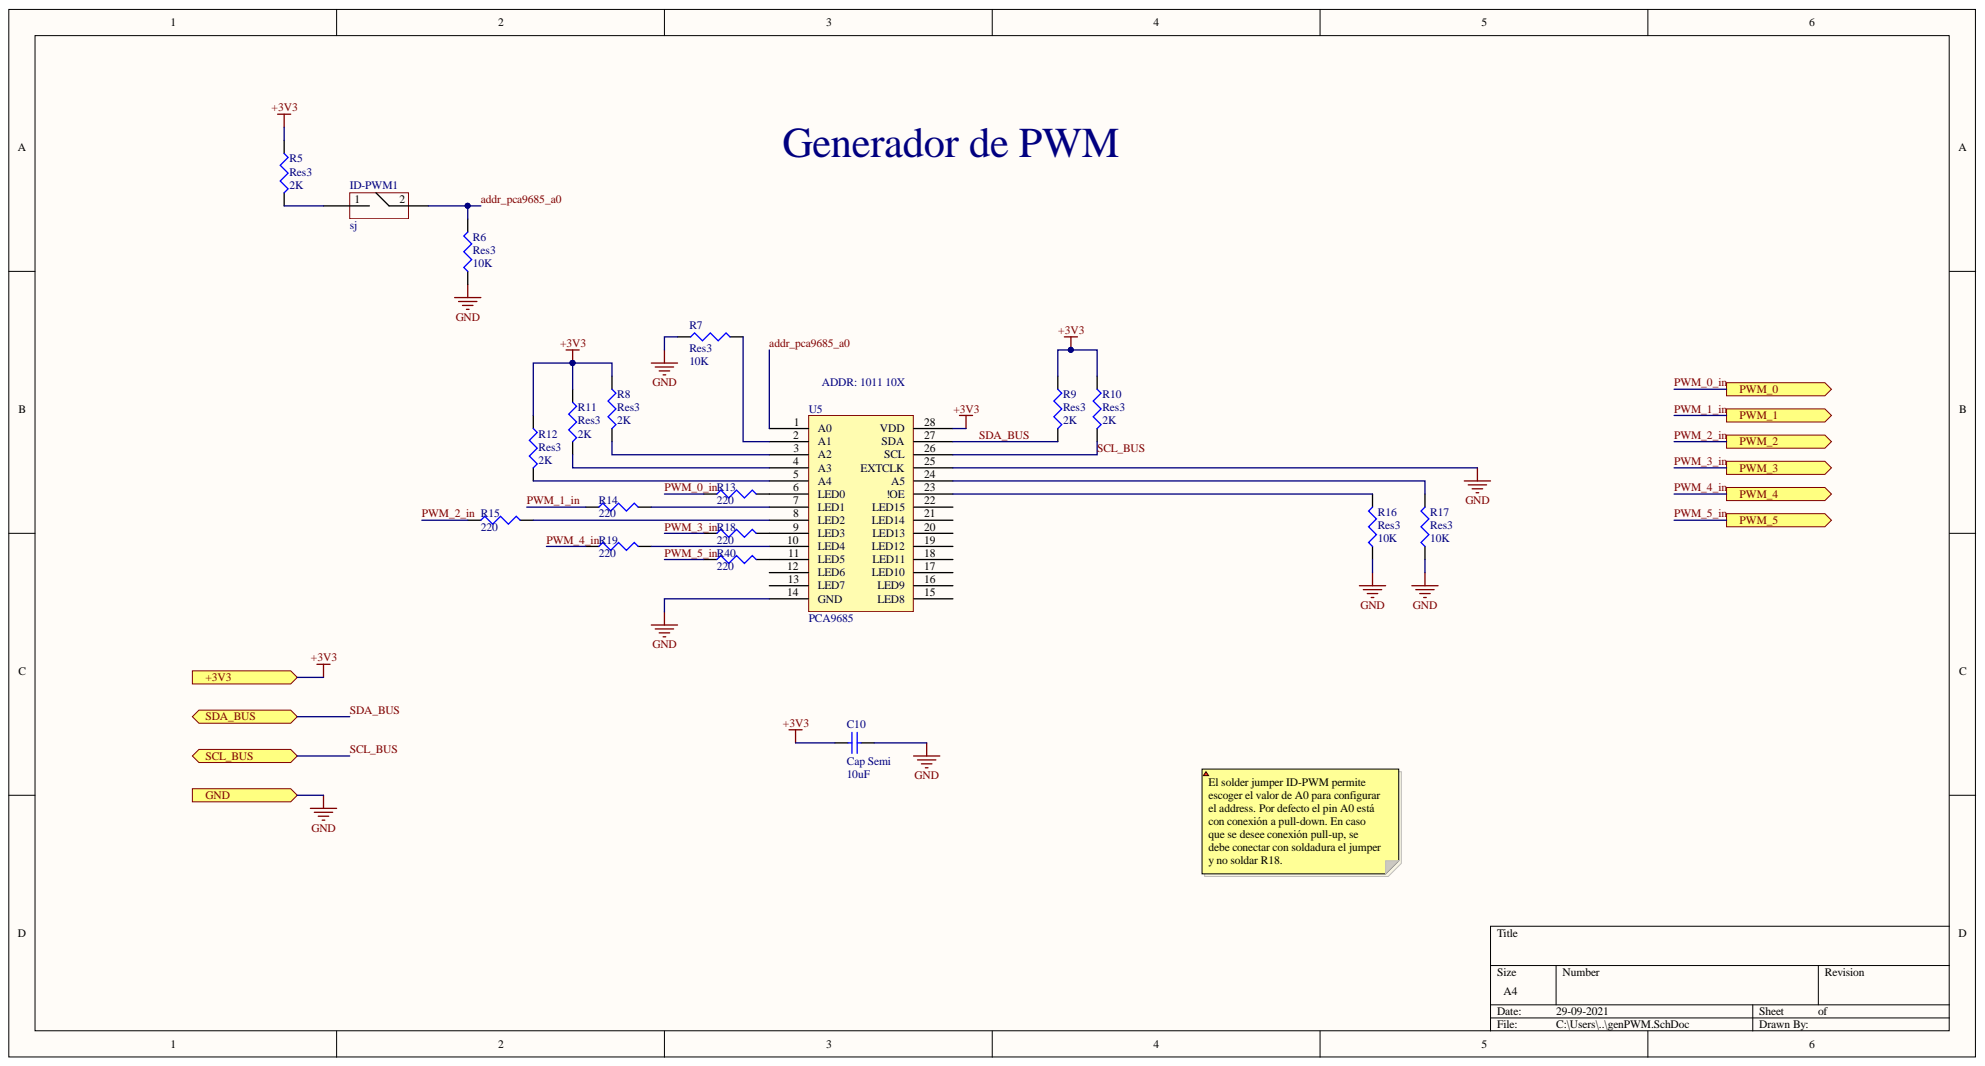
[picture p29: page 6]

El solder jumper ID-PWM permite
escoger el valor de A0 para configurar
el address. Por defecto el pin A0 está
con conexión a pull-down. En caso
que se desee conexión pull-up, se
debe conectar con soldadura el jumper
y no soldar R18.

Size A4 | Number | Revision

Date: 29-09-2021 | Sheet of
File: C:\Users\..\genPWM.SchDoc | Drawn By:

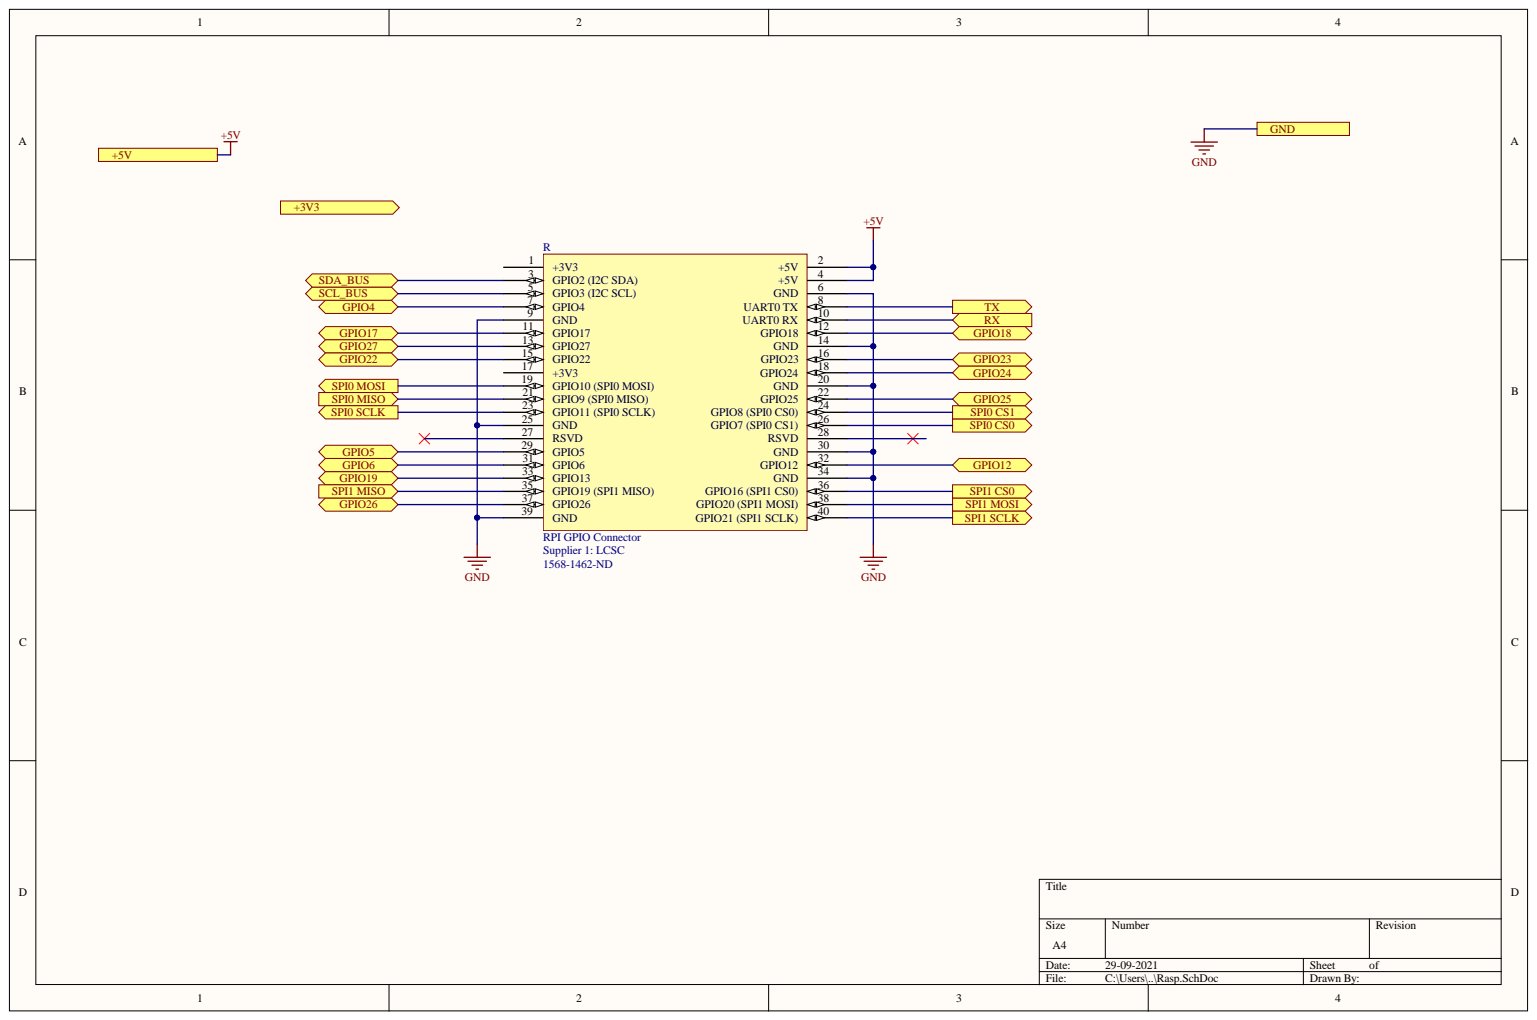
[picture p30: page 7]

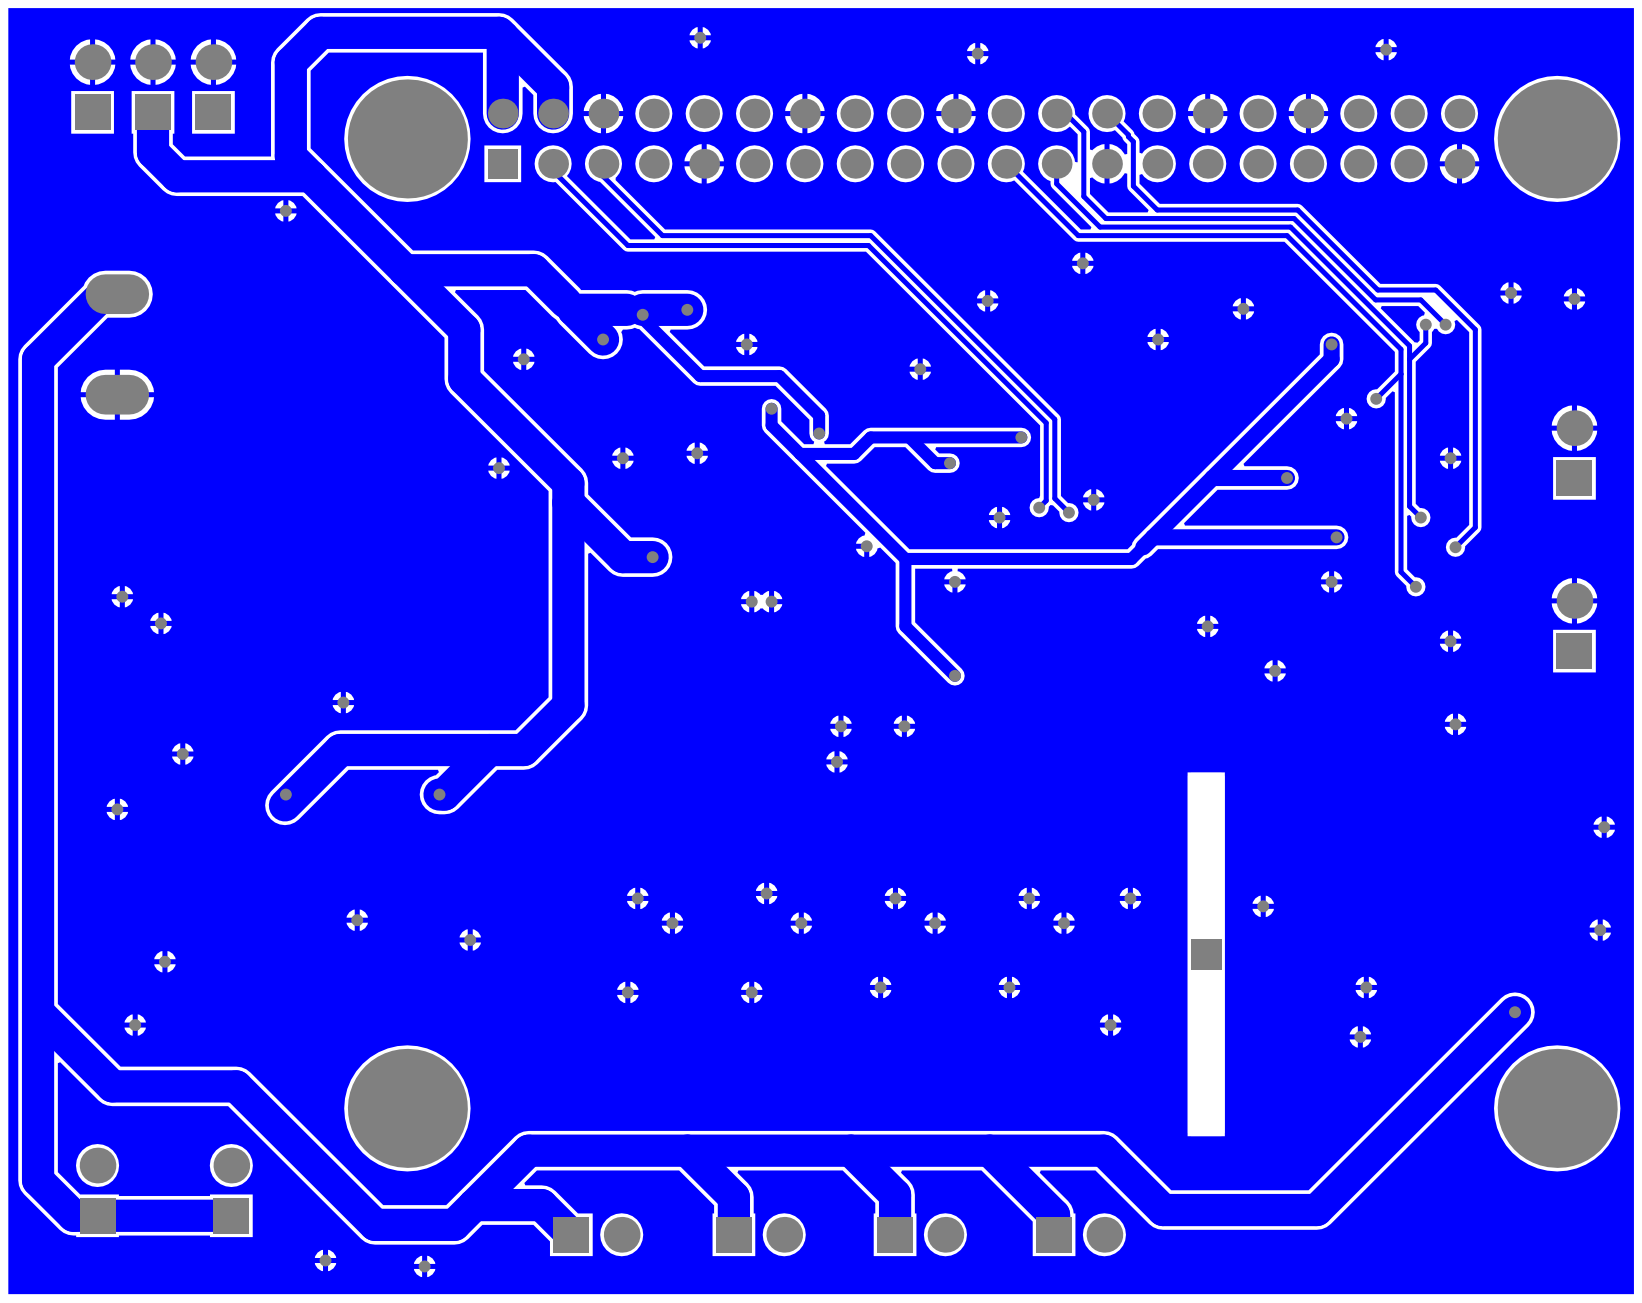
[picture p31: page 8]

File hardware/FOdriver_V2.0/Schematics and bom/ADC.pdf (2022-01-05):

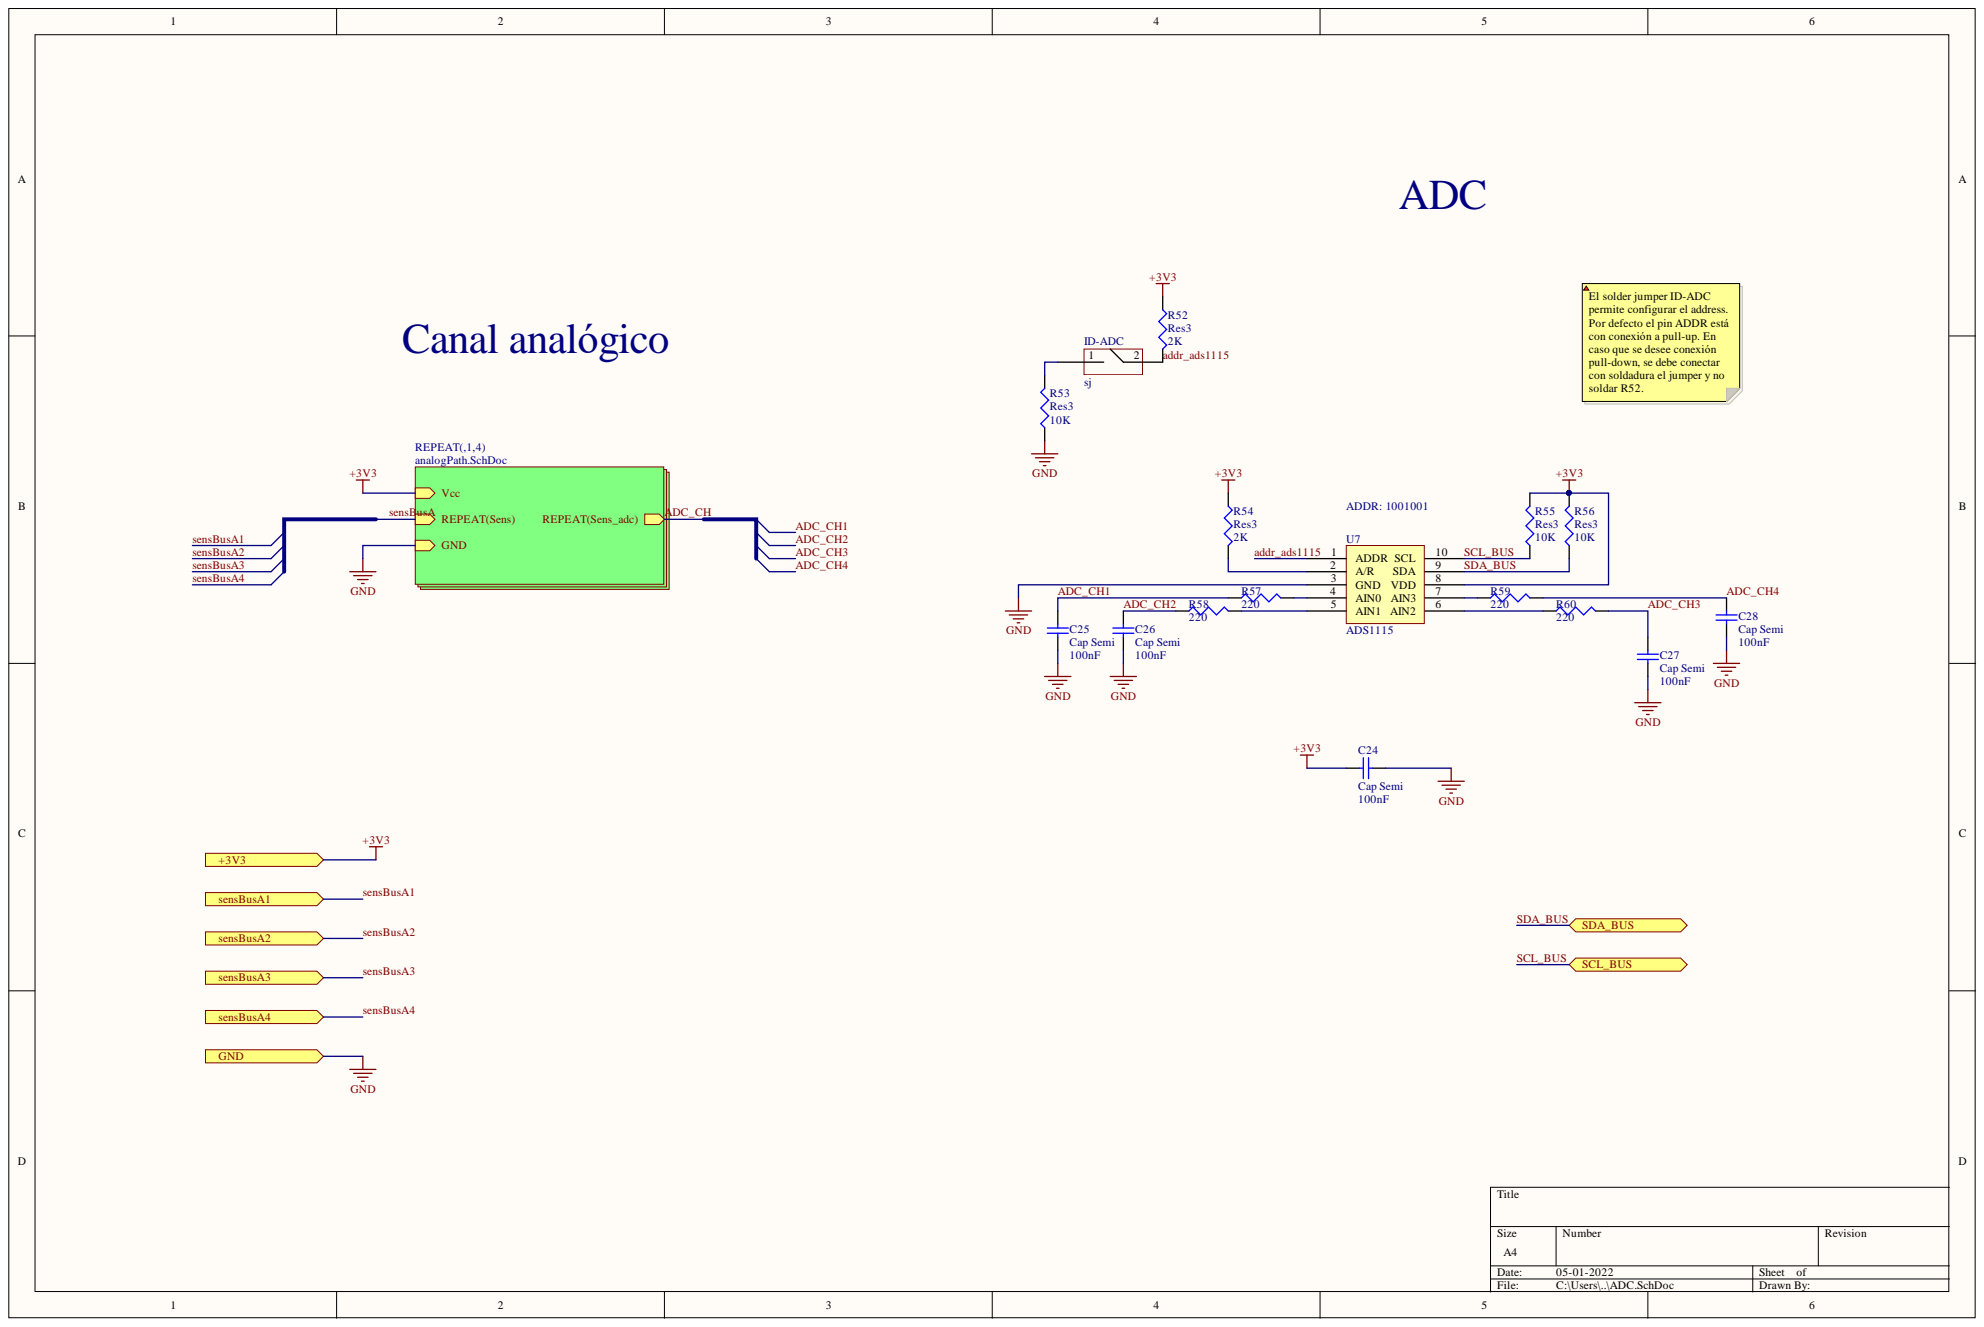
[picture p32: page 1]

El solder jumper ID-ADC
permite configurar el address.
Por defecto el pin ADDR está
con conexión a pull-up. En
caso que se desee conexión
pull-down, se debe conectar
con soldadura el jumper y no
soldar R52.

ADC_CH1 R57 | | AIN0 4

ADC_CH2 | 220 | AIN1 5

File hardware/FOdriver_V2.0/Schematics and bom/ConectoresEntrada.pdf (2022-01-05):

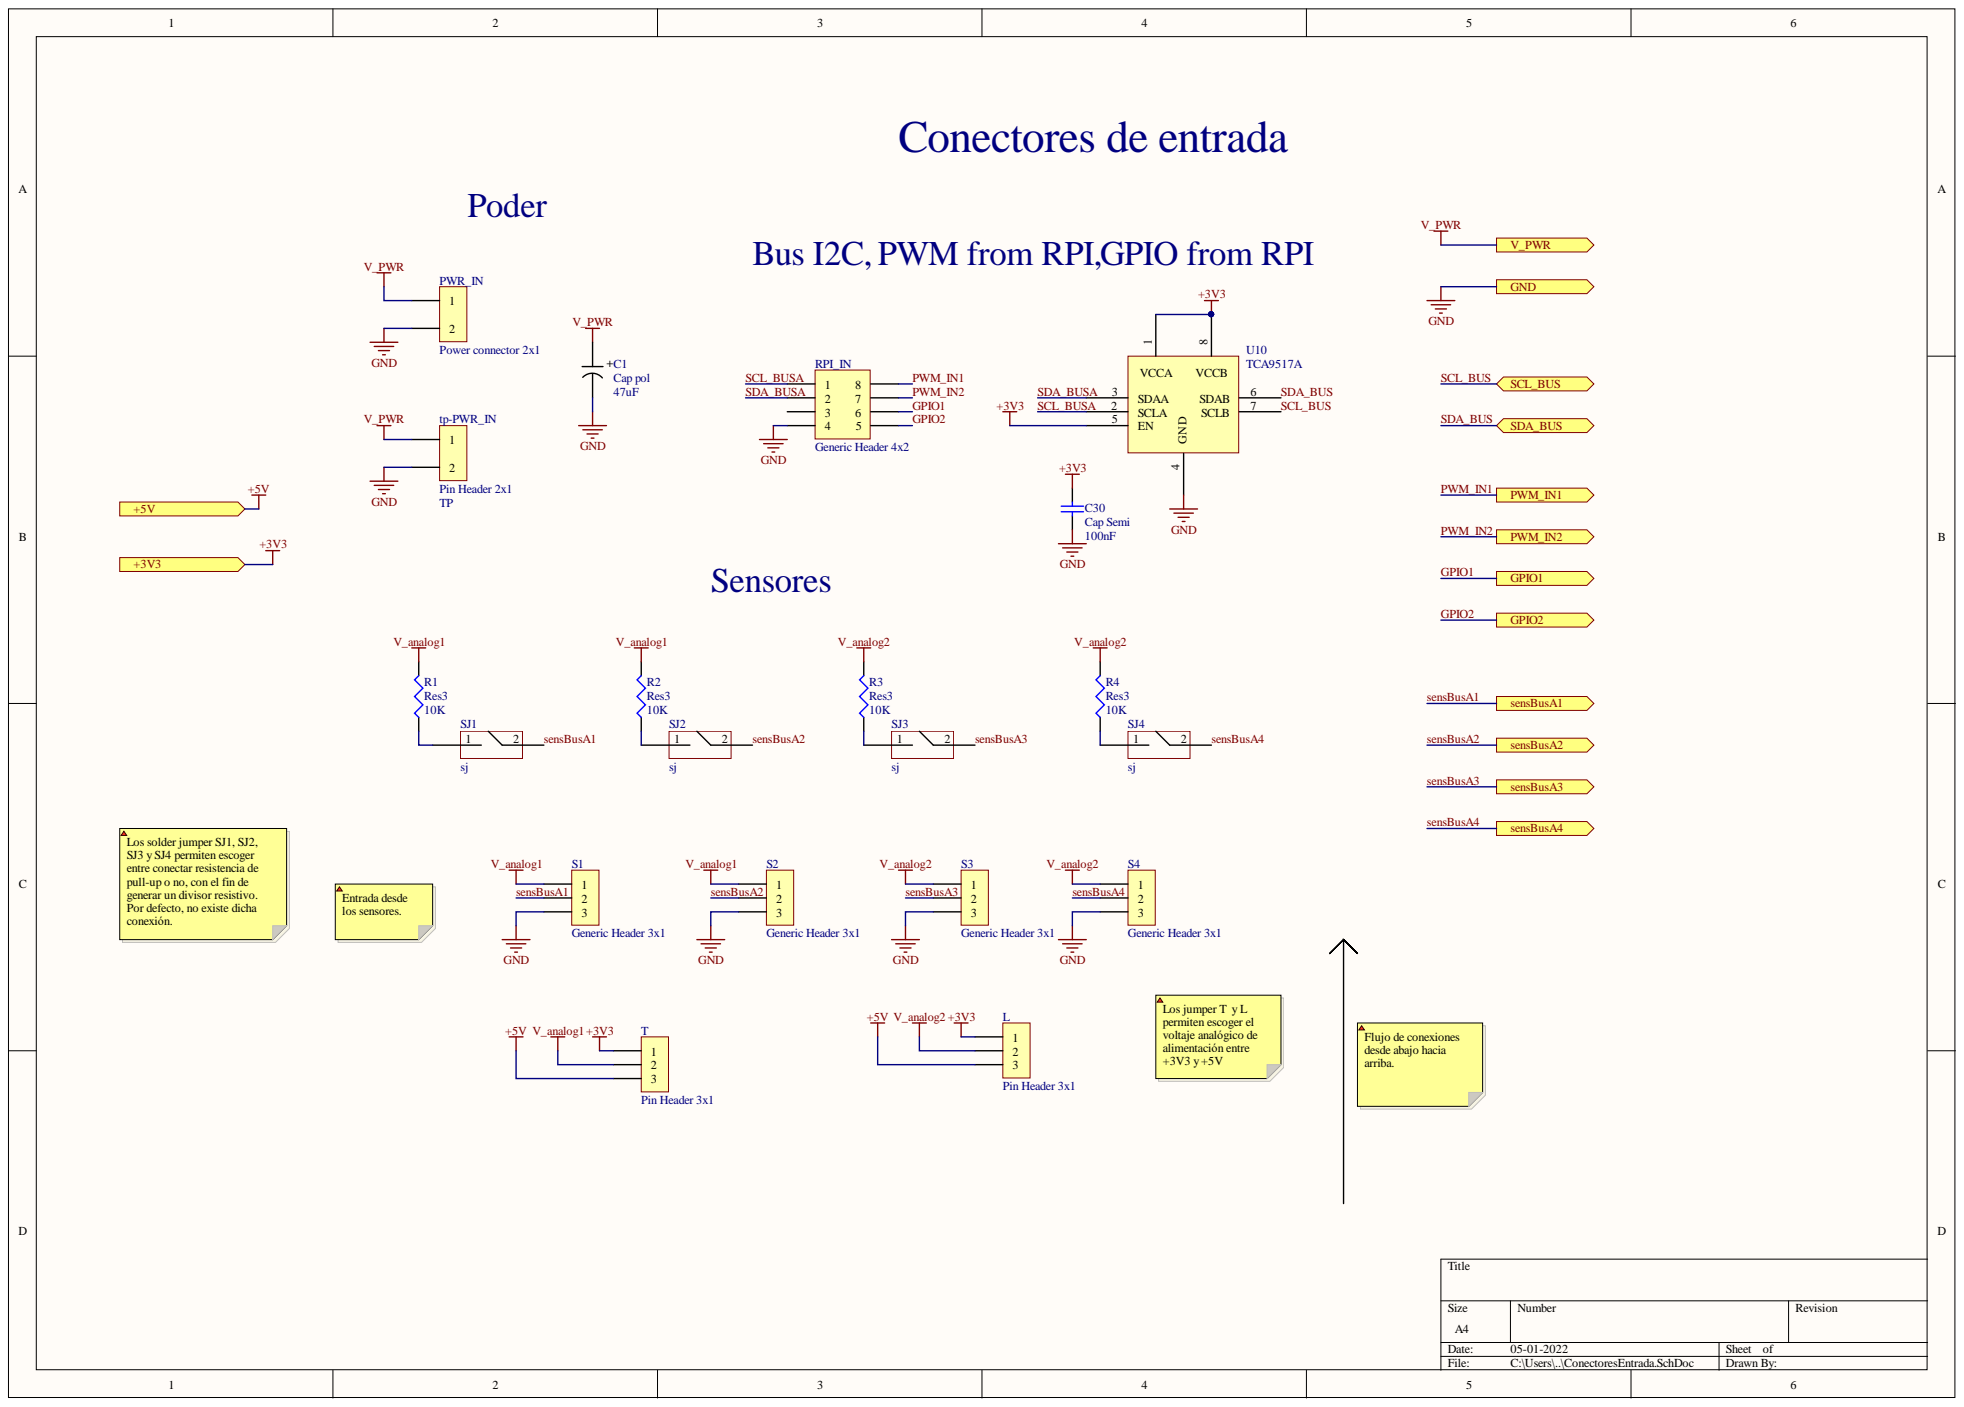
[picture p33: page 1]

Los solder jumper SJ1, SJ2,
SJ3 y SJ4 permiten escoger
entre conectar resistencia de
pull-up o no, con el fin de
generar un divisor resistivo.
Por defecto, no existe dicha
conexión.

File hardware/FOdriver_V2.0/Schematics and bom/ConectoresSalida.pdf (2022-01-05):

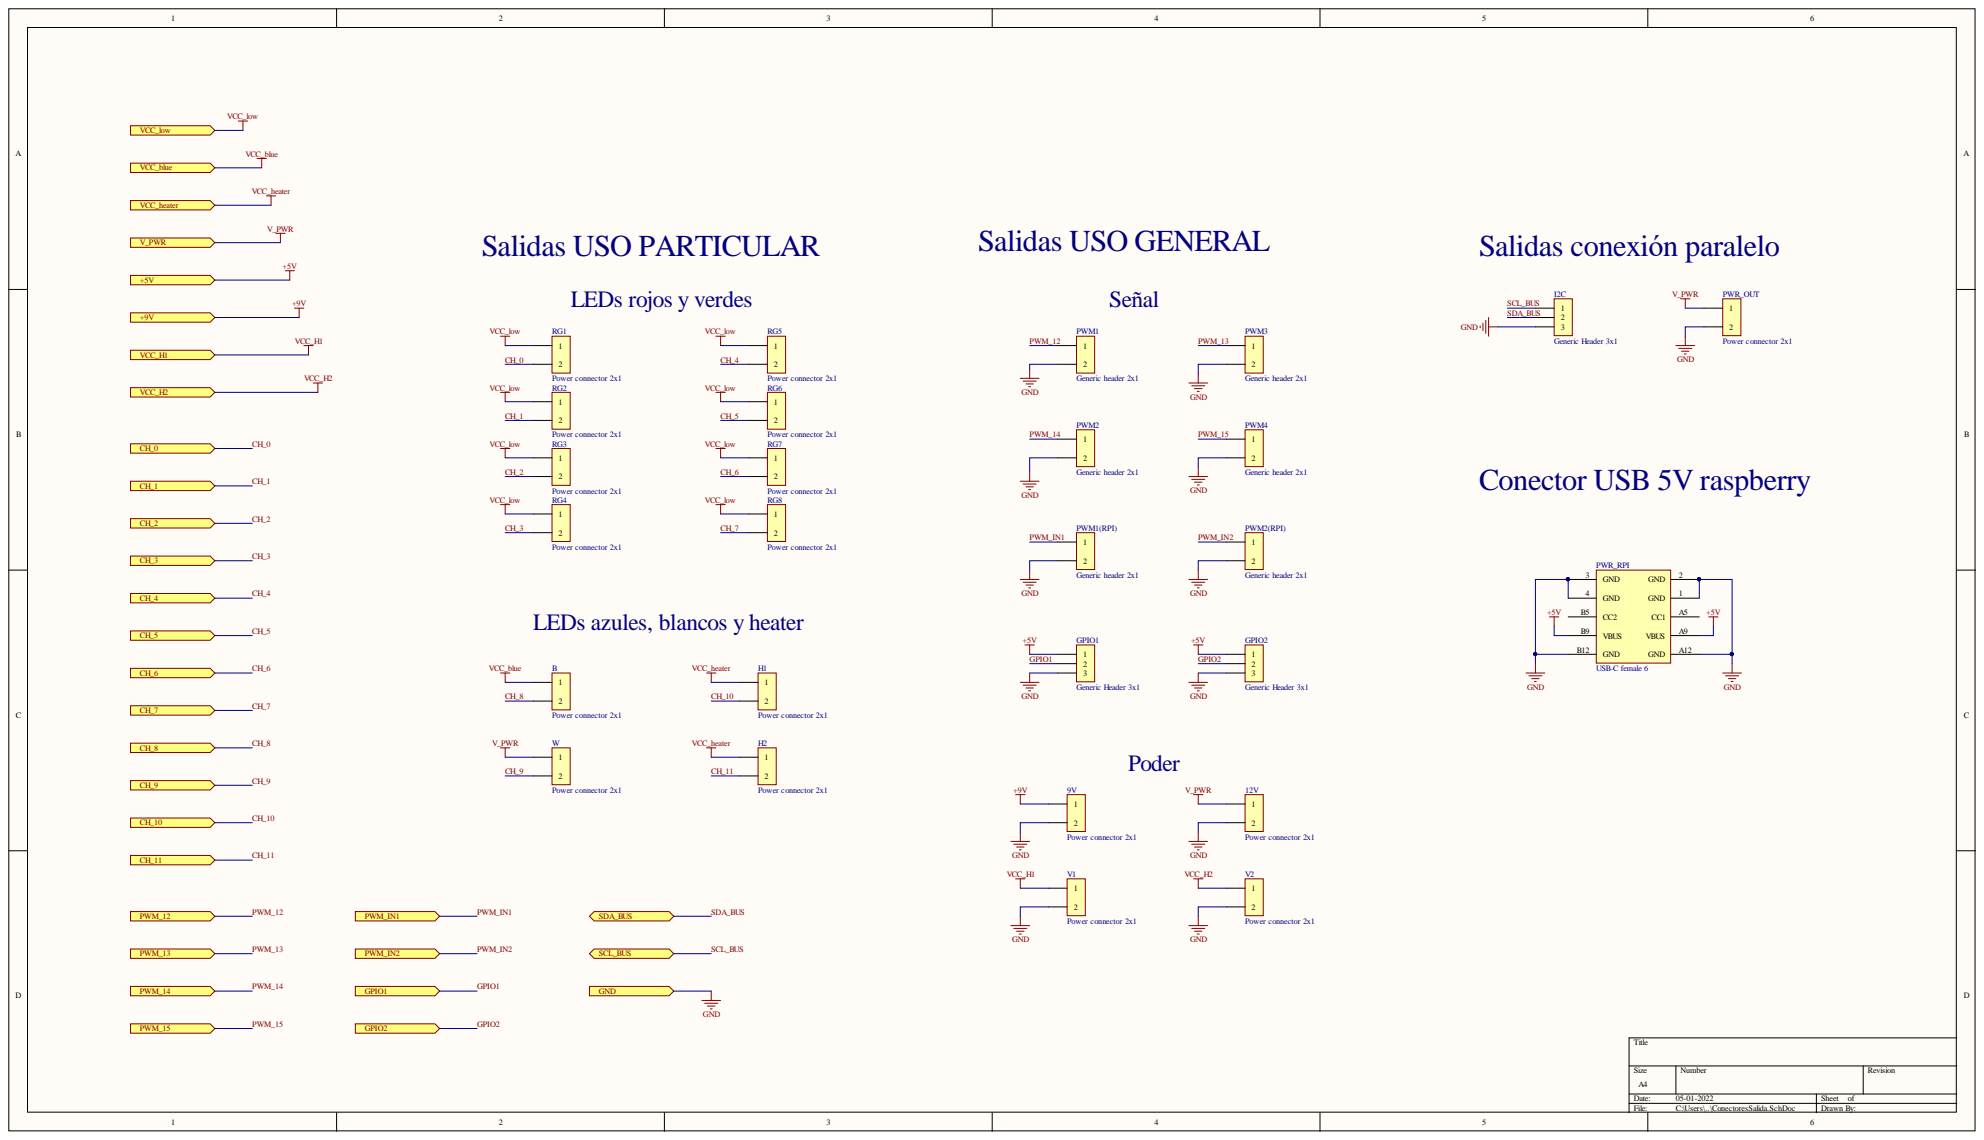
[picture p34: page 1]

LEDs azules, blancos y heater

Size A4 | Number | Revision

Date: 05-01-2022 | Sheet of
File: C:\Users\..\ConectoresSalida.SchDoc | Drawn By:

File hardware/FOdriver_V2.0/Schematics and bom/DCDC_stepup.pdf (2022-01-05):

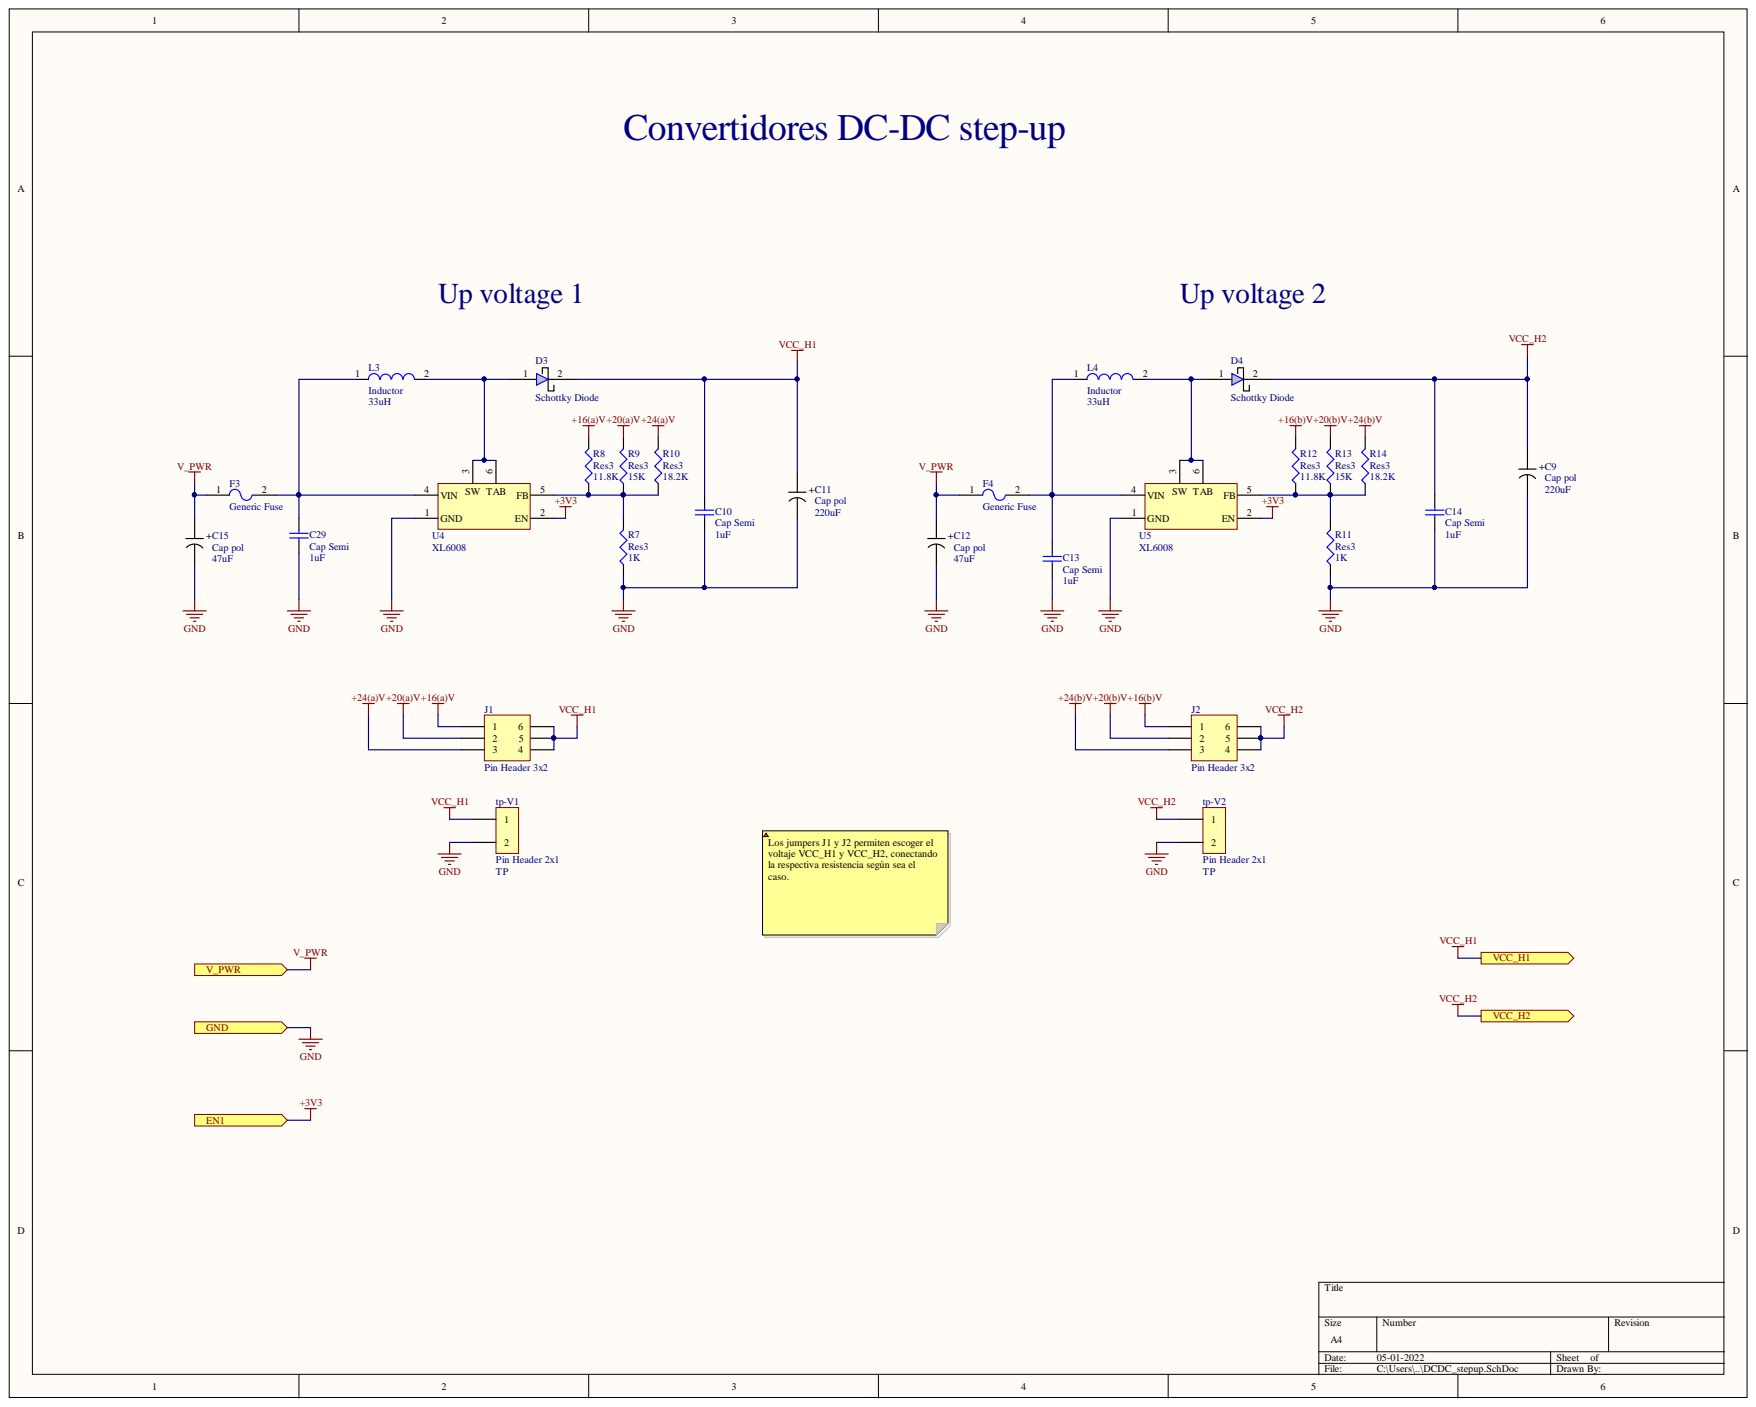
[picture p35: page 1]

Convertidores DC-DC step-up

Los jumpers J1 y J2 permiten escoger el
voltaje VCC_H1 y VCC_H2, conectando
la respectiva resistencia según sea el
caso.

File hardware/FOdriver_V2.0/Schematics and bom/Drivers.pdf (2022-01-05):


Driver de baja corriente

Drivers de alta corriente

Los jumper RG selector, Blue selector
y Heater selector permiten escoger el
voltaje VCC para alimentar la
configuración de LEDs rojos, verdes,
azules y los heaters.


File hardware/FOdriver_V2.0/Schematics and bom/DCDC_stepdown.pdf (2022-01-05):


Convertidores DC-DC step-down

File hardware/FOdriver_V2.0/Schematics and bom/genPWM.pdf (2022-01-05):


2 | | 2 7
3 | | 2 6 | S C L_ B U S
4 | | 2 5

S ize | N umber | Rev isi o n

0 5-0 1 -2 0 2 2 | S heet o f

F i le: C : \ Users\.. \gen PWM.S c h D o c | D raw n B y :


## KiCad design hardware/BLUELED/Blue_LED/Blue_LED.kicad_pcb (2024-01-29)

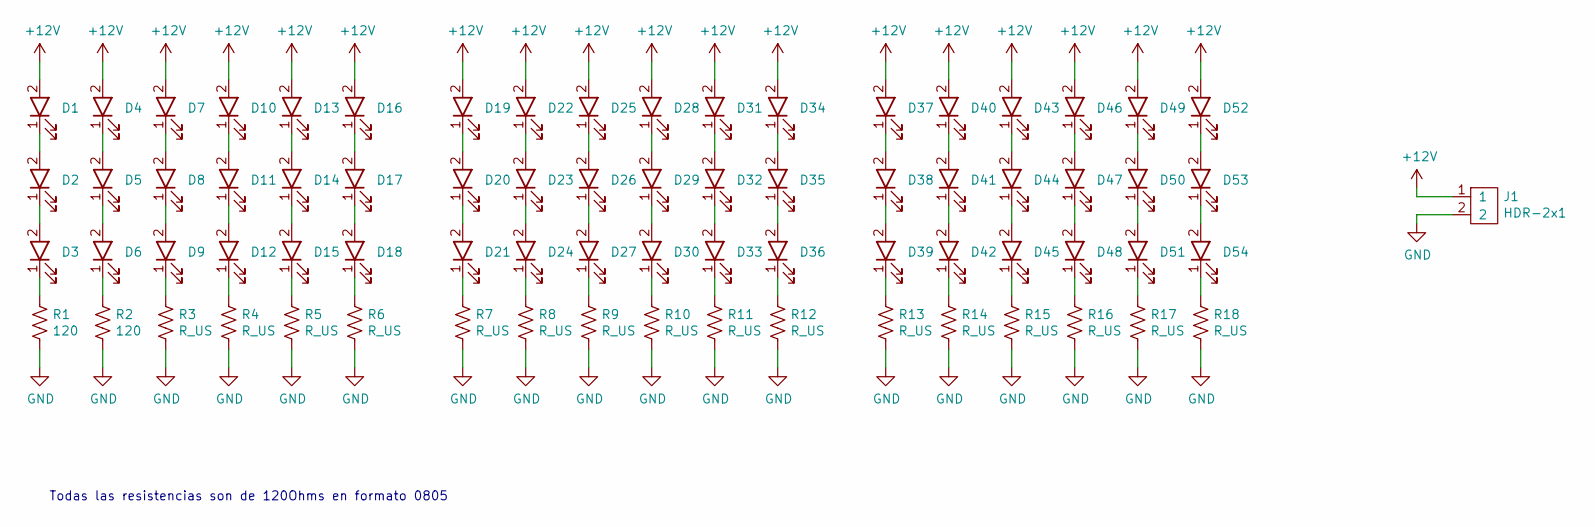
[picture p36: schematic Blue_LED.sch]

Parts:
D1, D2, D3, D4, D5, D6, D7, D8, D9, D10, D11, D12, D13, D14, D15, D16, D17, D18, D19, D20, D21, D22, D23, D24, D25, D26, D27, D28, D29, D30, D31, D32, D33, D34, D35, D36, D37, D38, D39, D40, D41, D42, D43, D44, D45, D46, D47, D48, D49, D50, D51, D52, D53, D54: LED; LED_5mm_TH_long
J1: HDR-2x1; JST-XH-2x1-2.5p-TH-V
R1, R2: 120; R_0805_2012Metric
R3, R4, R5, R6, R7, R8, R9, R10, R11, R12, R13, R14, R15, R16, R17, R18: R_US; R_0805_2012Metric

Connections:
+12V: D1.2, D4.2, D7.2, D10.2, D13.2, D16.2, D19.2, D22.2, D25.2, D28.2, D31.2, D34.2, D37.2, D40.2, D43.2, D46.2, D49.2, D52.2, J1.1
GND: J1.2, R1.2, R2.2, R3.2, R4.2, R5.2, R6.2, R7.2, R8.2, R9.2, R10.2, R11.2, R12.2, R13.2, R14.2, R15.2, R16.2, R17.2, R18.2
unnamed: D1.1, D2.2
unnamed: D2.1, D3.2
unnamed: D3.1, R1.1
unnamed: D4.1, D5.2
unnamed: D5.1, D6.2
unnamed: D6.1, R2.1
unnamed: D7.1, D8.2
unnamed: D8.1, D9.2
unnamed: D9.1, R3.1
unnamed: D10.1, D11.2
unnamed: D11.1, D12.2
unnamed: D12.1, R4.1
unnamed: D13.1, D14.2
unnamed: D14.1, D15.2
unnamed: D15.1, R5.1
unnamed: D16.1, D17.2
unnamed: D17.1, D18.2
unnamed: D18.1, R6.1
unnamed: D19.1, D20.2
unnamed: D20.1, D21.2
unnamed: D21.1, R7.1
unnamed: D22.1, D23.2
unnamed: D23.1, D24.2
unnamed: D24.1, R8.1
unnamed: D25.1, D26.2
unnamed: D26.1, D27.2
unnamed: D27.1, R9.1
unnamed: D28.1, D29.2
unnamed: D29.1, D30.2
unnamed: D30.1, R10.1
unnamed: D31.1, D32.2
unnamed: D32.1, D33.2
unnamed: D33.1, R11.1
unnamed: D34.1, D35.2
unnamed: D35.1, D36.2
unnamed: D36.1, R12.1
unnamed: D37.1, D38.2
unnamed: D38.1, D39.2
unnamed: D39.1, R13.1
unnamed: D40.1, D41.2
unnamed: D41.1, D42.2
unnamed: D42.1, R14.1
unnamed: D43.1, D44.2
unnamed: D44.1, D45.2
unnamed: D45.1, R15.1
unnamed: D46.1, D47.2
unnamed: D47.1, D48.2
unnamed: D48.1, R16.1
unnamed: D49.1, D50.2
unnamed: D50.1, D51.2
unnamed: D51.1, R17.1
unnamed: D52.1, D53.2
unnamed: D53.1, D54.2
unnamed: D54.1, R18.1

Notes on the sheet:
Todas las resistencias son de 120Ohms en formato 0805

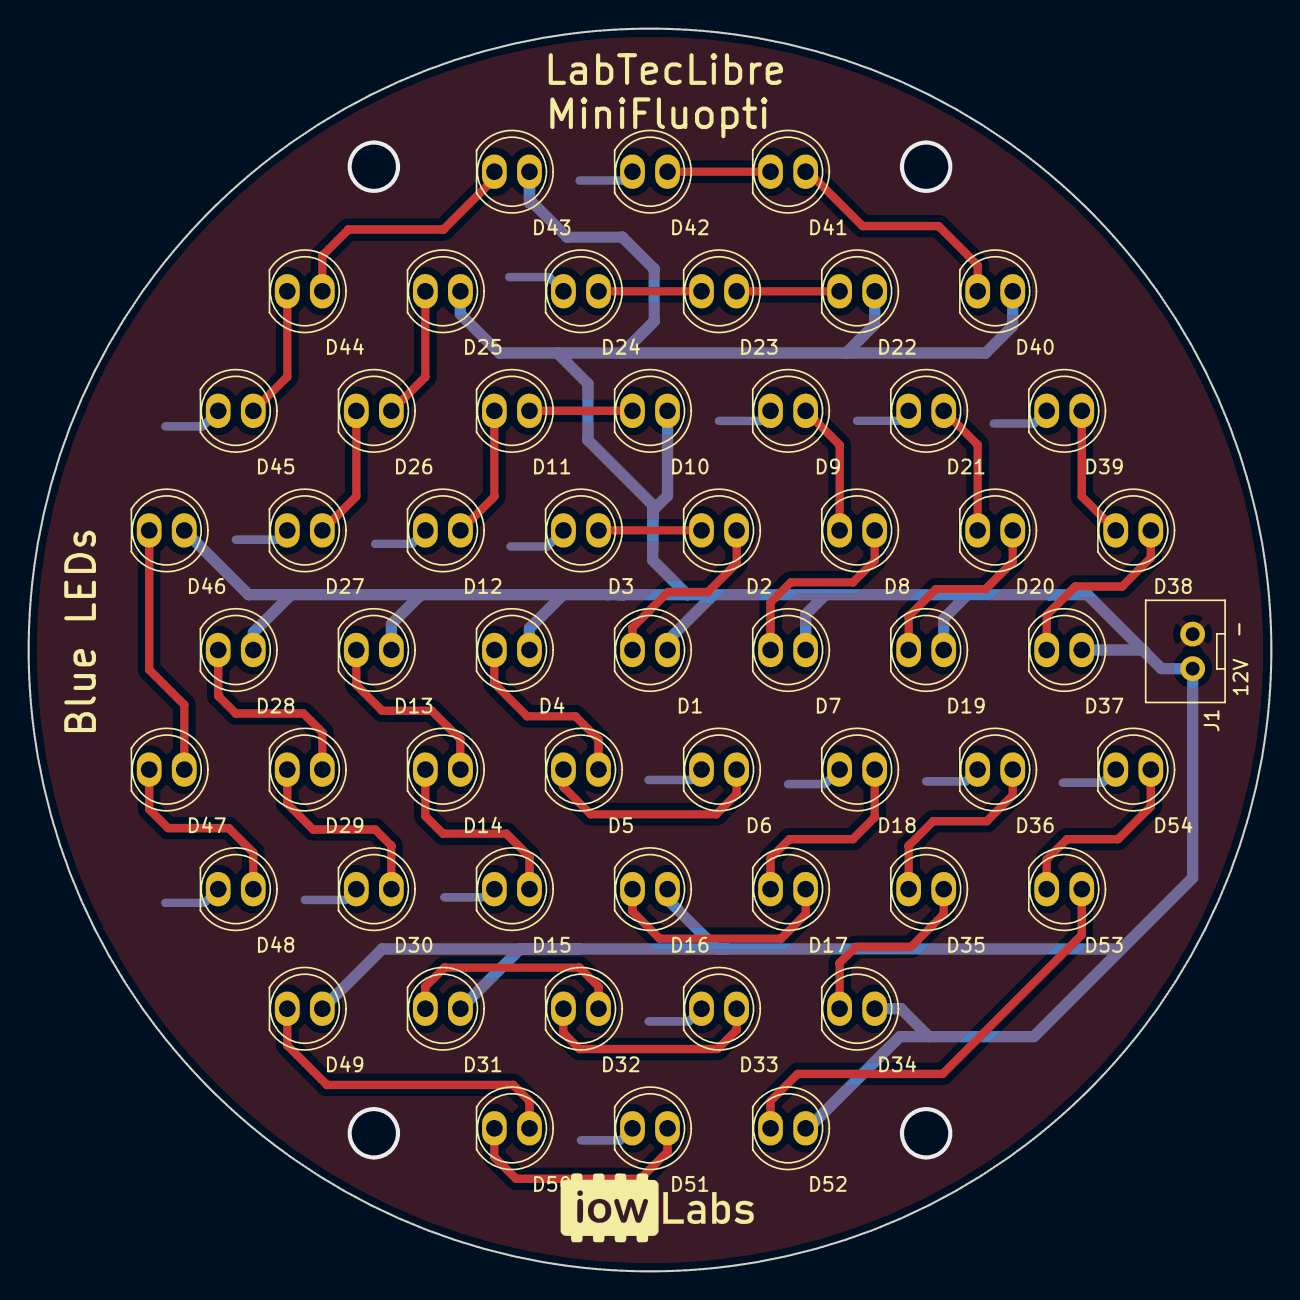
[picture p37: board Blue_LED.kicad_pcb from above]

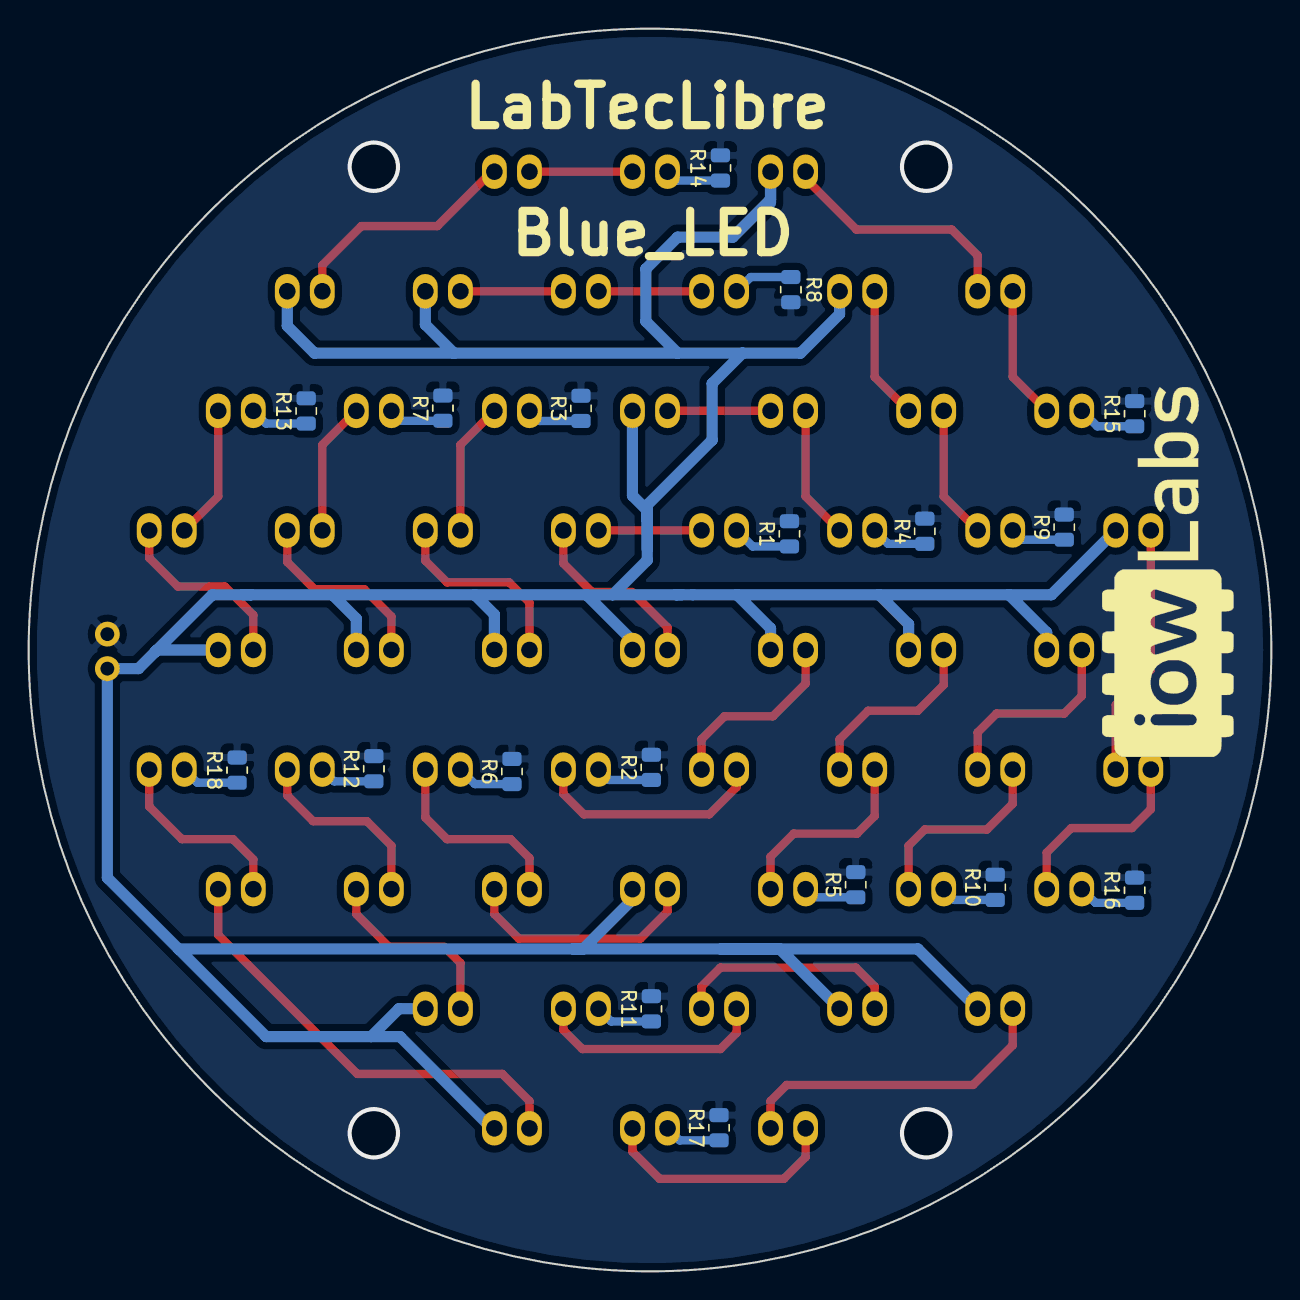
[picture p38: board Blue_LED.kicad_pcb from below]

Board: 2 copper layers, 90.0 x 90.0 mm, 73 parts (18 on the bottom side), 56 nets.

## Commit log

2020-12-16 testing Fluopti lib
    [Bill of Materials-PCBV2.xls]
2020-12-23 testing threads
2021-04-09 bom updated
    [ADC.SchDoc, BOM-updated.xlsx, ConectoresEntrada.SchDoc, DCDC_stepdown.SchDoc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]
2022-01-05 adding schematics pdf
    [Bill of Materials-PCBV2.xls]
2022-06-14 wac checkking repo
    [FOdriver_V2.0.PrjPcb]
2023-10-02 working on sample test!
2023-11-05 changing the folder order
    [ADC.SchDoc, BOM-updated.xlsx, Bill of Materials-PCBV2.xls, ConectoresEntrada.SchDoc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]
2023-11-29 Update software-readme.md
    Se completó un poco más la descripción de los preparativos de uso del software
2023-12-10 rearrange the modules attribute of Fluopti class and improve related functions as well as test. Also add a new rutine to turn ON leds manually
2023-12-20 simple_test changes
    [ADC.SchDoc, Bill of Materials-PCB1.xls, Blue LED.PrjPcb, BlueLed.SchDoc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]
2024-01-08 Update pi_adc.py
    correción de codigo a sensores
2024-01-12 modificación
    [FluOpti_V3.0.kicad_sch]
2024-01-23 pid funcional
    cambios en librerias realizados para su funcionamiento
    [datos_temperatura.csv]
2024-01-24 adding gui v1
    [015477608.stp, 2x_Male_Pin_2.54_mm.STEP, 430450212.stp, 69730.stp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]
2024-02-12 Nueva version fluopticontrolador para pruebas
2024-02-12 adding some documentation
    [FluOpti_V3.0.kicad_sch]
2024-02-13 implementacion de leds en interfaz y tiempo del bloque
2024-02-20 Nuevos archivos para cambio en interfaz post reunion
2024-02-21 board v3 minor changes
2024-02-22 Implementacion de nueva GUI en fluoControlador_v3 y avance en Configuracion de patrones de fotos
2024-02-23 arreglo temporal a LEDoff
2024-02-23 comento un timer para debugear mas facil
2024-02-23 Se agrega el configurador de patrones
2024-02-23 debug camera
2024-02-23 fix bug paramtros camera
2024-03-15 updating temp control on gui
    [FluOpti_V3.0-B_Cu.gbl, FluOpti_V3.0-B_Mask.gbs, FluOpti_V3.0-B_Paste.gbp, FluOpti_V3.0-B_Silkscreen.gbo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]
2024-03-30 adding openSCAD and STLs
    [FluOpti_Main.scad, circle_diffuser_holder.scad, circle_diffuser_holder_centered.stl, cone.stl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]
2024-04-07 minor corrections to make them work wirh the new FluOpti methods
2024-04-07 change the invalid temperature measurement value from -1 to 100, then the heater stops if this measurement fails
2025-03-12 correct openscad
    [Flat_cam_holder.scad, FluOpti_Main.scad]
2025-04-07 add separate base
    [FluOpti_Main_Wsf.scad]
2025-04-24 new designs and STLs folder
    [FluOpti_Main_Wsf.scad, base_holder.stl, circle_diffuser_holder_centered.stl, cone.stl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]
